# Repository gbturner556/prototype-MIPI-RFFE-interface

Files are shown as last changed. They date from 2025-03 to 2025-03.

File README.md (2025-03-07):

# MIPI-RFFE-interface-board
Gavin Turner  
<gbturner@gmail.com>

## Background
This project was built by Gavin Turner in the summer of 2022 during an 
internship at GlobalFoundries' electrical failure analysis lab. The goal 
of the project was to develop a simple communications interface that would
allow for quick screening of product fallout through die level probing.
The interface was built specifically for the communications through
the MIPI RFFE protocol as outlined by the MIPI alliance, but software 
modifications could allow for communciations with any protocol requiring
four channels or less.

## Stakeholder Specifications
- Implement easy to use functions for **read**, **extended read**, **write**, **extended write**, **bus park**, and **assert SSC**
- Supply and monitor **VDD** and **VIO** (1V to 3.3V up to 5mA)
- Adjustable logic levels on **DATA** and **CLK** pins (1V to 3.3V)
- Utilize an RP2040 microcontroller
- Implement solution on a PCB with BNC connectors for ease of use with micromanipulators during probing

## Implementation
The core of the software solution is an API implemented through the use of a C++ header file.
This header file defines a custom class named `RFFE_master`. This class builds upon a variety
of private functions to enable the user to "bit bang" dataframes with occordance to the MIPI
alliance specifications. The software allows for low speed communications with a DUT with active
power supply monitoring to characterize defective parts. The final software solution can be viewed
in the **MIPI.h** and **MIPI.cpp** files as well as application examples in the **source_code** folder.

The hardware solution implements 4 MCP4725 ADC's for variable logic levels and power supplies, 2
INA219 current shunts monitors for active power supply monitoring, 1 OLED display for data output,
1 TCA9548 I2C multiplexer to manage communications with peripherals, and 5 BNC connectors for easy
connection to micromanipulators. All components are integrated on a standalone PCB with an on board
RP2040 based microcontroller. The final hardware implementation can be viewed in the **board_files** folder

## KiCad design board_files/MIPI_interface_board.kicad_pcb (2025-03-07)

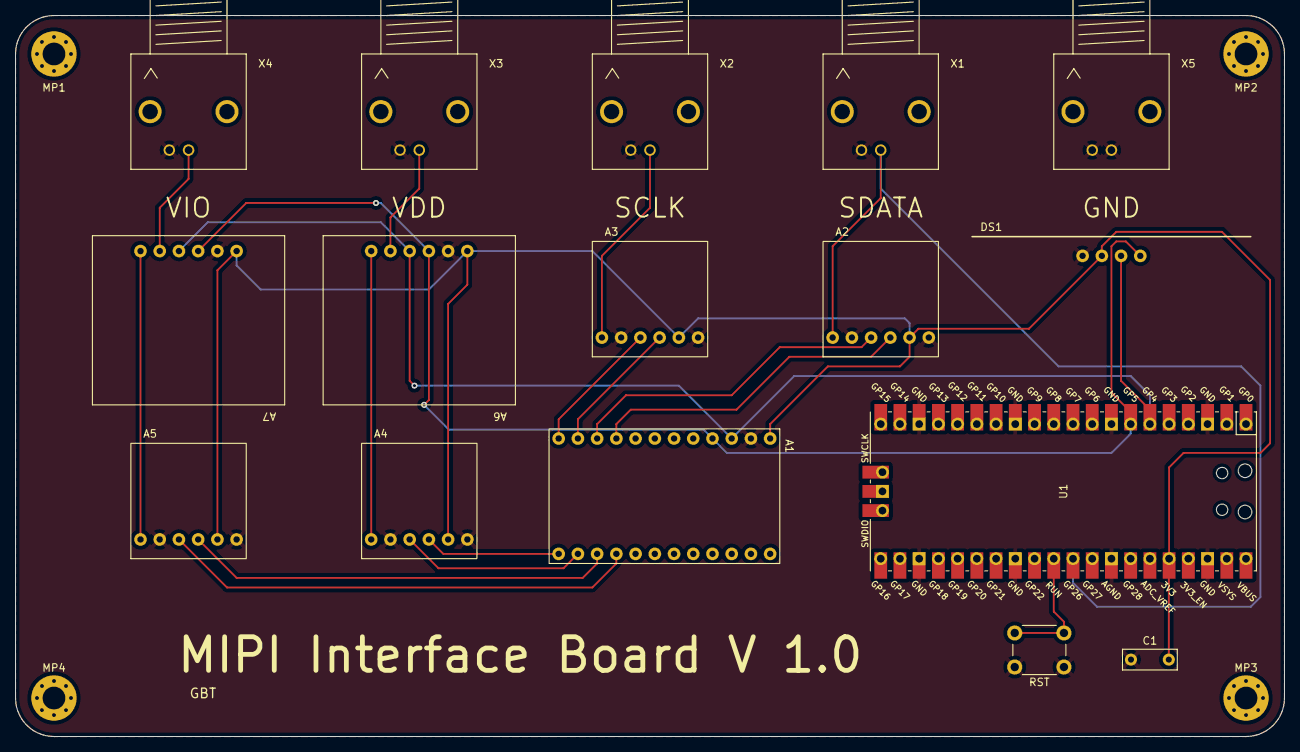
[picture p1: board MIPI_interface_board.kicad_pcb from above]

Board: 2 copper layers, 167.6 x 95.2 mm, 20 parts (0 on the bottom side), 19 nets.

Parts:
A1: TCA9548; TCA9548-BOB
A2, A3, A4, A5: MCP4725; MCP4725-BOB
A6, A7: INA219; INA219-BOB
C1: 0.22 uF; C_Rect_L7.0mm_W2.5mm_P5.00mm
DS1: OLED; OLED-BOB
MP1, MP2, MP3, MP4: MountingHole_3mm_Pad_Via
RST: RST; SW_PUSH_6mm_H5mm
U1: Pico; RPi_Pico_SMD_TH
X1, X2, X3, X4, X5: CONBNC002; BNC-CONBNC002-THT-90

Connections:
+3.3V: A1.1 (VIN), A2.5 (VCC), A3.5 (VCC), A4.5 (VCC), A5.5 (VCC), A6.1 (VCC), A7.1 (VCC), C1.2, DS1.2 (3V3), U1.36 (3V3)
/SCLK_MAIN: A1.4 (SCL), A6.4 (SDA), A7.4 (SDA), DS1.4 (SCL), U1.7 (GPIO5)
/SCL_OUT: A3.1 (OUT), X2.1 (SIG)
/SDATA_MAIN: A1.3 (SDA), A6.3 (SCL), A7.3 (SCL), DS1.3 (SDA), U1.6 (GPIO4)
/SDA_OUT: A2.1 (OUT), U1.31 (GPIO26_ADC0), X1.1 (SIG)
/VCC_OUT: A6.5 (VIN-), X3.1 (SIG)
/VIO_OUT: A7.5 (VIN-), X4.1 (SIG)
/~RESET: RST.2, U1.30 (RUN)
GND: A1.2 (GND), A2.2 (GND), A2.6 (GND), A3.2 (GND), A3.6 (GND), A4.2 (GND), A4.6 (GND), A5.2 (GND), A5.6 (GND), A6.2 (GND), A7.2 (GND), C1.1, DS1.1 (GND), RST.1, U1.3 (GND), U1.8 (GND), U1.13 (GND), U1.18 (GND), U1.23 (GND), U1.28 (GND), U1.33 (AGND), U1.38 (GND), X1.2 (GND), X2.2 (GND), X3.2 (GND), X4.2 (GND), X5.1 (SIG), X5.2 (GND)
unnamed: A1.9 (SD0), A2.4 (SDA)
unnamed: A1.10 (SC0), A2.3 (SCL)
unnamed: A1.11 (SD1), A3.4 (SDA)
unnamed: A1.12 (SC1), A3.3 (SCL)
unnamed: A1.13 (SD2), A4.4 (SDA)
unnamed: A1.14 (SC2), A4.3 (SCL)
unnamed: A1.15 (SD3), A5.4 (SDA)
unnamed: A1.16 (SC3), A5.3 (SCL)
unnamed: A4.1 (OUT), A6.6 (VIN+)
unnamed: A5.1 (OUT), A7.6 (VIN+)

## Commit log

2025-03-02 board files added
    [MIPI_interface_board.kicad_pcb, MIPI_interface_board.kicad_sch]
2025-03-03 added board symbols and footprints
2025-03-07 completed README and added corrected versions of board files (no trace rounding)
    [MIPI_interface_board.kicad_pcb]
